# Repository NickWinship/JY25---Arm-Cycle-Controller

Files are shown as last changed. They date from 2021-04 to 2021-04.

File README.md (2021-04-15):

# Xbox One Arm-Cycle-Controller

The Xbox One Arm-Cycle-Controller is an exercise device that interfaces with the Xbox Adaptive Controller to produce an interactive fitness experience targeted towards users with spinal cord injuries. 

The device functions as an electromechanical adapter that adds controller functionality to a commercial mini-exercise bicycle through the use of control signals derived from encoder and inertial measurements. The control signals are interpreted by the Xbox Adaptive Controller as joystick and trigger inputs, allowing the device to play racing games on Xbox One Series consoles or Windows 10 PCs.

## Project Background
Individuals with physical disabilities often have limited options to be physically active. A popular form of cardiovascular exercise for people with Spinal Cord Injuries (SCIs) is ‘hand cycling’. At the Physical Activity Research Centre (PARC), users with SCIs can engage in many physical exercise activities while building social connections within their community. 

With the ongoing COVID-19 situation and the initial closure of PARC, it was clear that there was a need for a new home-based exercise device for individuals with SCIs. The goal of this Capstone project, was to develop an Arm Cycle Controller, compatible with the Xbox adaptive controller for Xbox One Series consoles and Windows 10 PCs. The final product is aimed at bringing an inexpensive and engaging exercise experience into the end user’s home, one that can foster community through online engagement. 

## Compatibility
| Device | Version | Additional Information|
|--------|---------|-----------------------|
|Xbox Console| One Series | |
| PC | Windows 10.0 | |

## Download
| Resrouce | Version | Format | Link |
|----------|---------|--------|------|
| PCB Files |
| Firmware |
| PCB Housing |
| MPU6050 Housing |
| Encoder Mount |

## Resources
| Resrouce | Link |
|----------|------|
| Project Instrucable| https://www.instructables.com/How-to-Build-Your-Xbox-One-Arm-Cycle-Adaptive-Cont/ |
|Project Video | https://www.youtube.com/watch?v=MWBfiwAXUjg |

## Contributers
***Clients/Sponsers:***
<ul>
  <li>PARC (Physical Activity Research Centre) [https://icord.org/parc/]</li>
  <li>Makers Making Change [https://www.makersmakingchange.com/]</li>
  <li>Microsoft [https://www.microsoft.com/en-us/accessibility]</li>
</ul>

***Capstone Students:***
<ul>
  <li>Scott Beaulieu [nicholassjbeaulieu@protonmail.com]</li>
  <li>Edward Luo [luohaoubc@gmail.com]</li>
  <li>Keith Consolacion [keithcon@student.ubc.ca]</li>
  <li>Fabian Lozano [fabian.lozano@protonmail.com]</li>
  <li>Nicholas Winship [nick.winship@outlook.com]</li>
</ul>

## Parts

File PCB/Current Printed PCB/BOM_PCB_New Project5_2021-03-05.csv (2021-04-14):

ID | Name | Designator | Footprint | Quantity | Manufacturer Part | Manufacturer | Supplier | Supplier Part | JLCPCB SMD | LCSC Assembly | Assembly Type | Paste Type
1 | WJ128V-5.0-3P | E1 | CONN-TH_3P-P5.00_WJ128V-5.0-3P | 1 | WJ128V-5.0-3P | ReliaPro | LCSC | C8270 |  | Yes | manualWeld | expand
2 | WJ128V-5.0-2P | E2 | CONN-TH_2P-P5.00_WJ128V-5.0-2P | 1 | WJ128V-5.0-2P | ReliaPro | LCSC | C8269 |  | Yes | manualWeld | expand
3 | DB125-3.81-4P | IMU,JJ1 | CONN-TH_DB125-3.81-4P | 2 | DB125-3.81-4P | DIBO | LCSC | C395880 |  | Yes | manualWeld | expand
4 | PJ313D | JL1,JR1 | AUDIO-TH_PJ313D | 2 | PJ313D | BOOMELE | LCSC | C18167 |  | Yes | manualWeld | expand
5 | 1K | J1,J2,L1,L3,R1,R3 | R0603 | 6 | 0603WAF1001T5E | UniOhm | LCSC | C21190 | Yes | Yes | smtWeld | base
6 | 10K | J3,J4,L2,R2 | R0603 | 4 | 0603WAF1002T5E | UniOhm | LCSC | C25804 | Yes | Yes | smtWeld | base
7 | TEENSY 4.0 W/O int Pins | T1 | TEENSY 4.0 W/O INT PINS | 1 | Teensy 4.0 | PJRC

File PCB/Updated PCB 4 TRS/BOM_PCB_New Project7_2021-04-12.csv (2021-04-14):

ID | Name | Designator | Footprint | Quantity | Manufacturer Part | Manufacturer | Supplier | Supplier Part | Price | LCSC Assembly | Assembly Type | Paste Type | JLCPCB SMD
1 | WJ128V-5.0-3P | E1 | CONN-TH_3P-P5.00_WJ128V-5.0-3P | 1 | WJ128V-5.0-3P | ReliaPro | LCSC | C8270 | 0.1393 | Yes | manualWeld | expand
2 | WJ128V-5.0-2P | E2 | CONN-TH_2P-P5.00_WJ128V-5.0-2P | 1 | WJ128V-5.0-2P | ReliaPro | LCSC | C8269 | 0.091 | Yes | manualWeld | expand
3 | DB125-3.81-4P | IMU | CONN-TH_DB125-3.81-4P | 1 | DB125-3.81-4P | DIBO | LCSC | C395880 | 0.1909 | Yes | manualWeld | expand
4 | 10K | J2,J5,L2,R2 | R0603 | 4 | 0603WAF1002T5E | UniOhm | LCSC | C25804 | 0.001 | Yes | smtWeld | base | Yes
5 | 1K | J1,J3,J4,J6,L1,L3,R1,R3 | R0603 | 8 | 0603WAF1001T5E | UniOhm | LCSC | C21190 | 0.001 | Yes | smtWeld | base | Yes
6 | PJ313D | JL,JR,JR1,JR2 | AUDIO-TH_PJ313D | 4 | PJ313D | BOOMELE | LCSC | C18167 | 0.057 | Yes | manualWeld | expand
7 | TEENSY 4.0 W/O int Pins | T | TEENSY 4.0 W/O INT PINS | 1 | Teensy 4.0 | PJRC

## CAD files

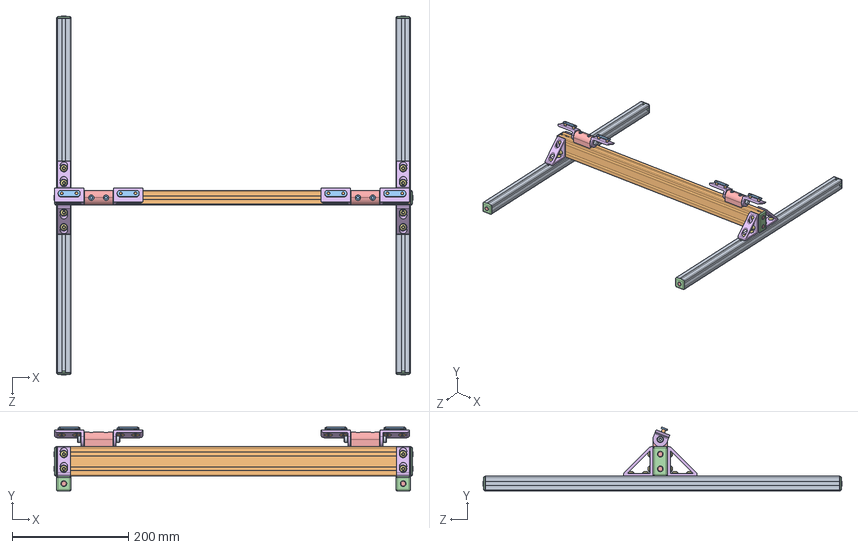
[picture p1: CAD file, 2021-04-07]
3D Prints/Arm Cycle Mount Models/Arm Cycle Controller.sldasm
618.1 x 110.1 x 618.1 mm
SHCS x 4
Dynamic L Pivot Arms x 4
10S Large Washer x 4
10S Small Washer x 4
Socket Head Shoulder Screw_AI x 4
Socket Countersunk Head Cap Screw_AI x 8
TSLOT ENDCAPS x 6
Inside Corner Gussets x 4
Socket Button Head Cap Screw_AI x 16

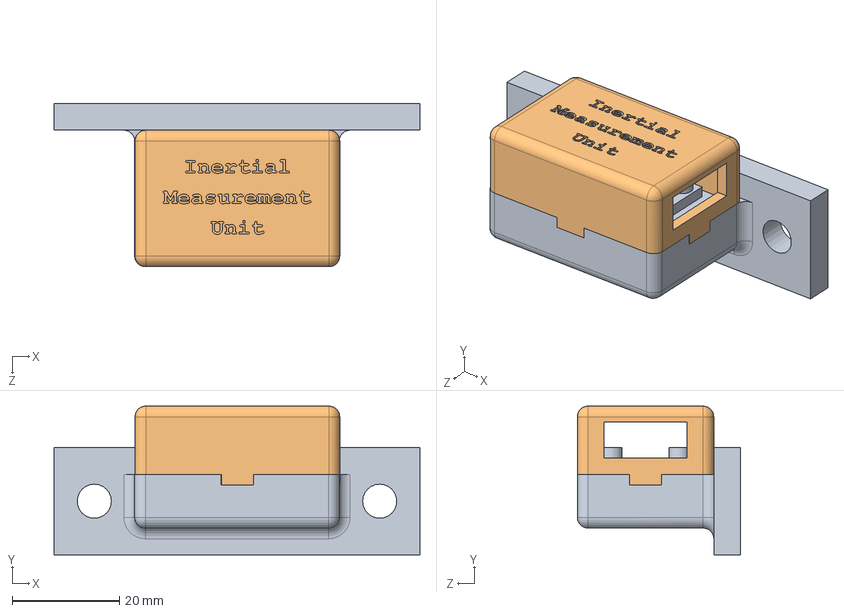
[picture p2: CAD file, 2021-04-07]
3D Prints/MPU6050 Mount Models/MPU6050 Mount Assembly.SLDASM
68.1 x 27.7 x 30.4 mm
MPU6050 Mount
Cover

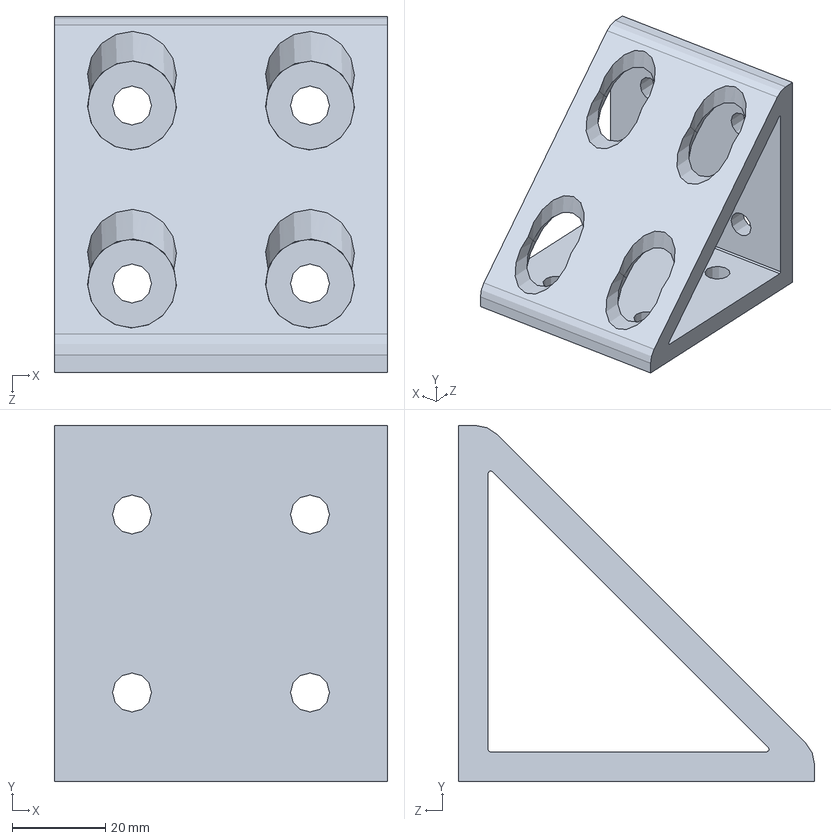
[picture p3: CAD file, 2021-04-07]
3D Prints/Arm Cycle Mount Models/Inside Corner Gussets.SLDASM
71.4 x 76.2 x 76.2 mm

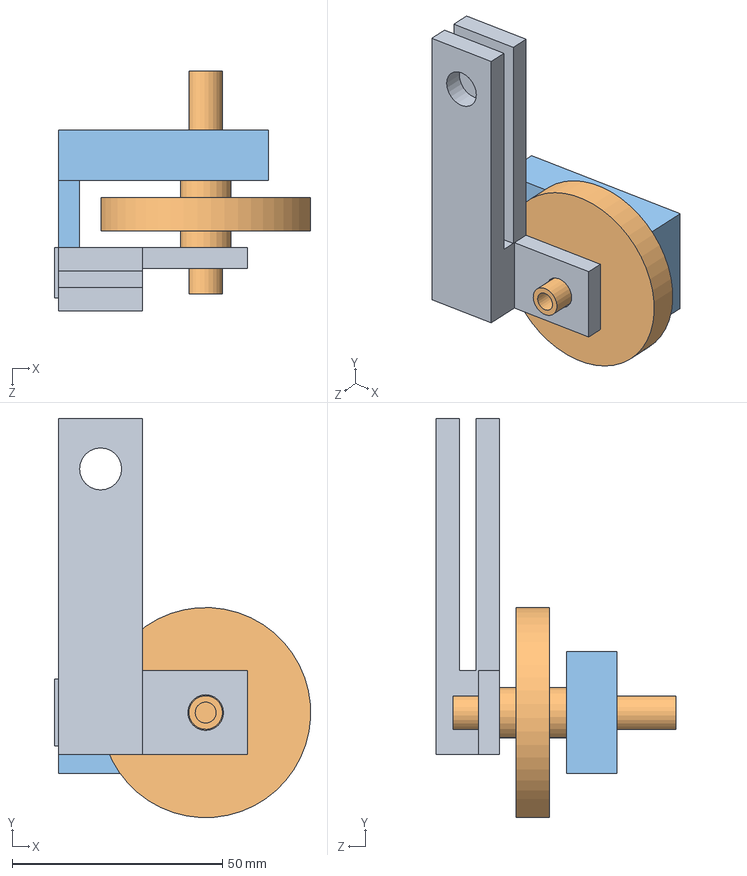
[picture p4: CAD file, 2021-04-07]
3D Prints/Encoder Mount Models/Encoder Attatchment Assembly.SLDASM
61.0 x 94.9 x 57.0 mm
Mounting
Gear
Wheel support

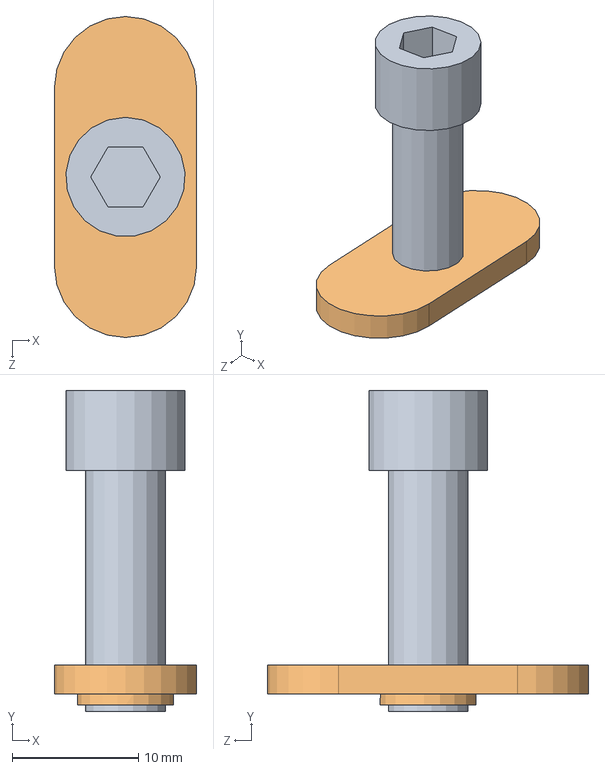
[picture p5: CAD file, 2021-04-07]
3D Prints/Arm Cycle Mount Models/SHCS Assembly.SLDASM
11.3 x 25.4 x 25.4 mm
SHCS
Economy T-nuts

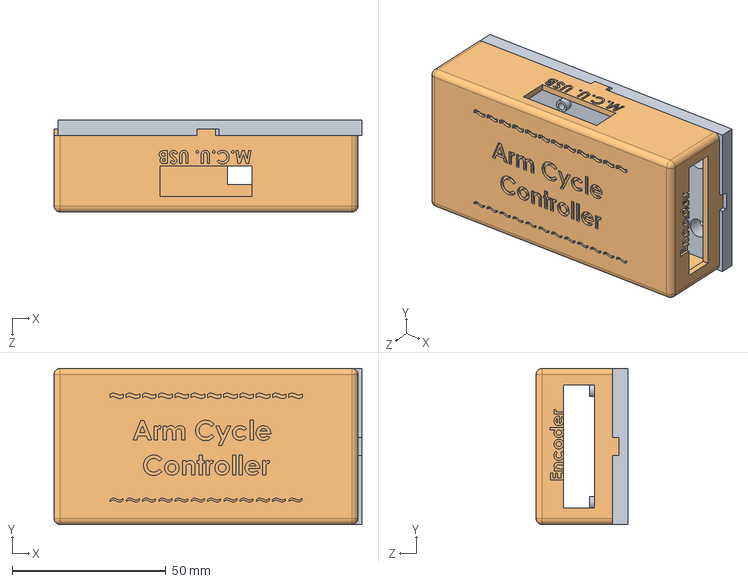
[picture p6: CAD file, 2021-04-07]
3D Prints/PCB Mount Models/PCB Mount Assembly.SLDASM
100.3 x 50.8 x 30.0 mm
PCB Mount
PCB Cover

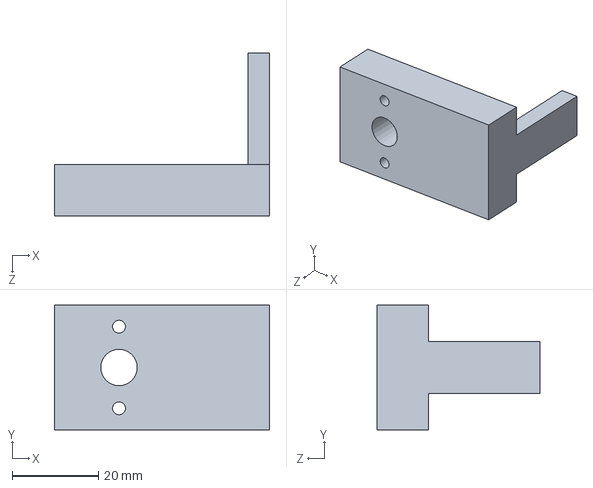
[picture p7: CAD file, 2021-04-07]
3D Prints/Encoder Mount Models/Wheel support.SLDPRT
50.0 x 29.0 x 38.0 mm

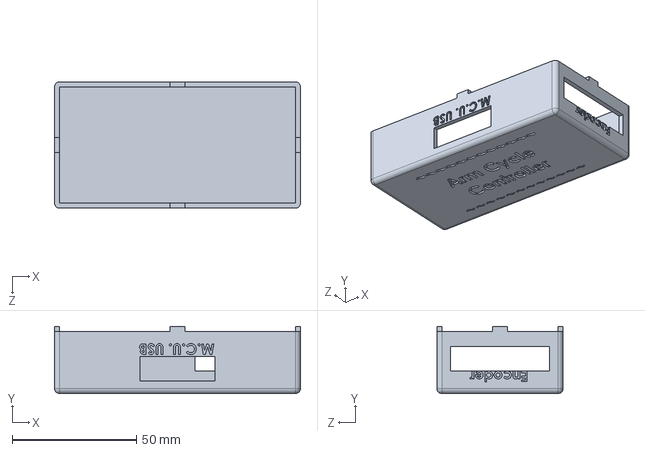
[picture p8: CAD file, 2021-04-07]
3D Prints/PCB Mount Models/PCB Cover.SLDPRT
99.0 x 27.0 x 50.8 mm

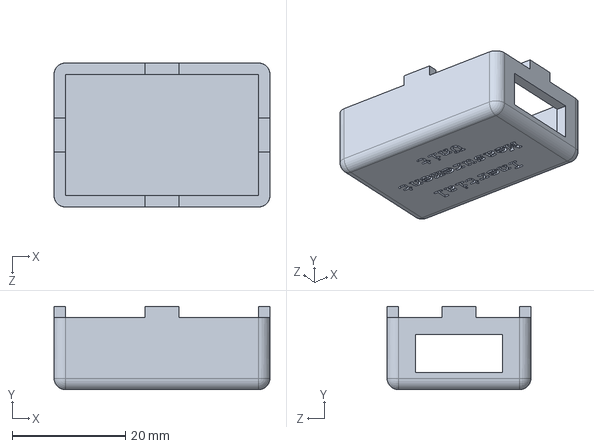
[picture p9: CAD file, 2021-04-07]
3D Prints/MPU6050 Mount Models/Cover.SLDPRT
38.1 x 14.7 x 25.4 mm

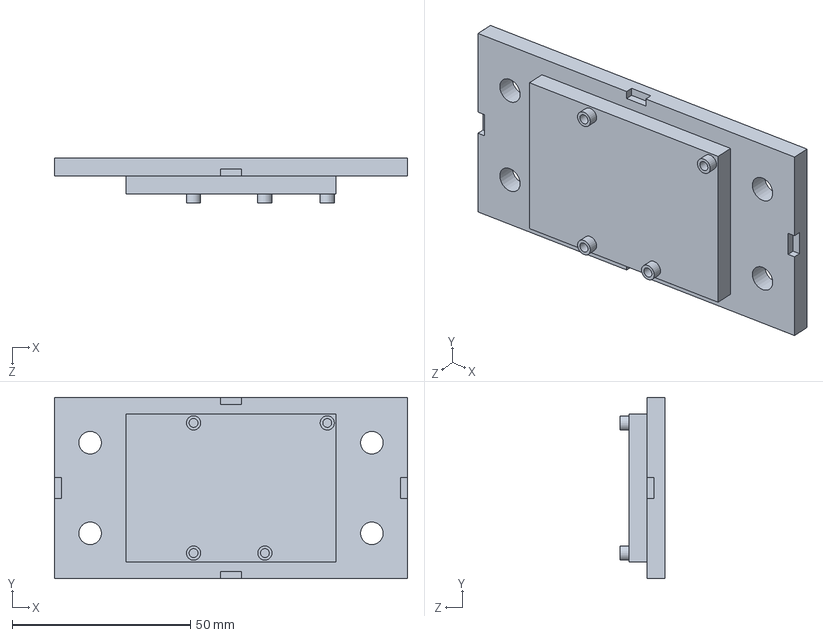
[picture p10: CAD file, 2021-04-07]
3D Prints/PCB Mount Models/PCB Mount.SLDPRT
99.0 x 50.8 x 12.5 mm

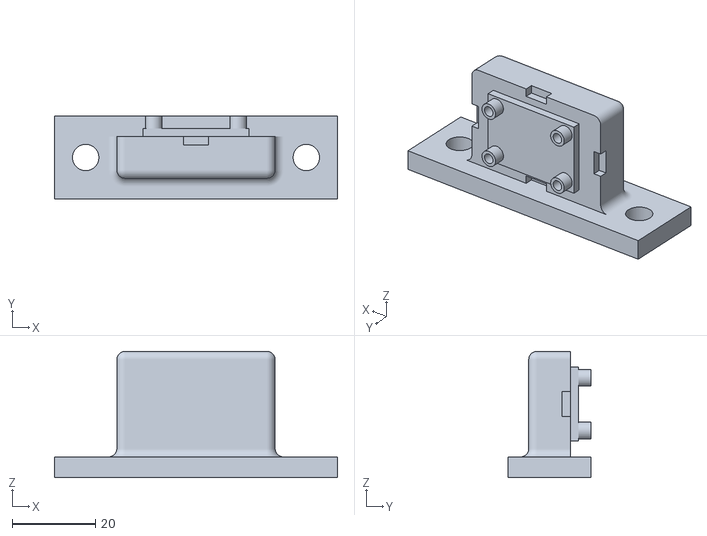
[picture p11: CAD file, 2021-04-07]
3D Prints/Project STL Files/IMU_Mount_1.STL
68.1 x 20.0 x 30.4

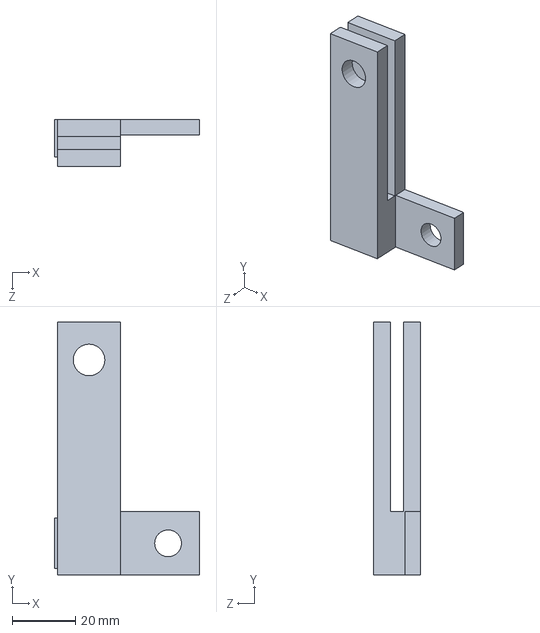
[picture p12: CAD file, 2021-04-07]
3D Prints/Encoder Mount Models/Mounting.SLDPRT
46.0 x 80.0 x 15.0 mm

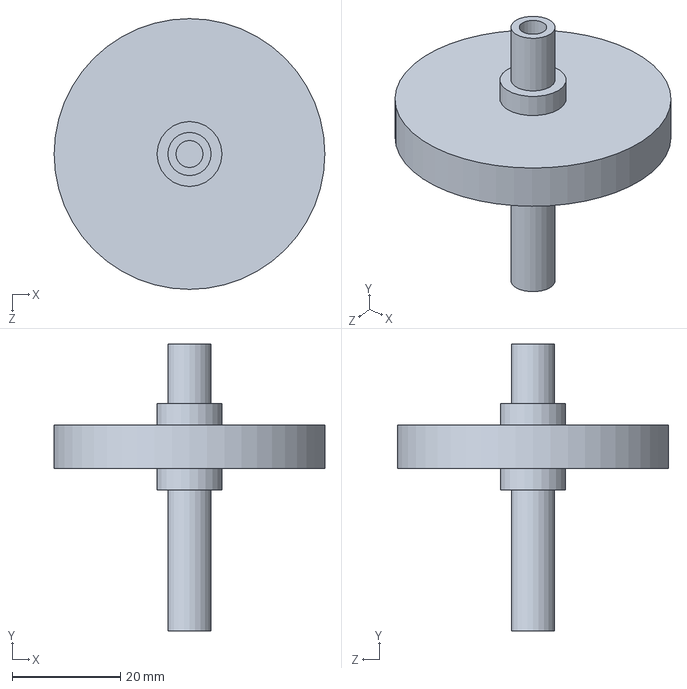
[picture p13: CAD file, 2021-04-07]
3D Prints/Encoder Mount Models/Gear.SLDPRT
50.0 x 53.0 x 50.0 mm

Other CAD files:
3D Prints/Project STL Files/PCB_Mount_2.STL
3D Prints/MPU6050 Mount Models/MPU6050 Mount.SLDPRT
3D Prints/Project STL Files/Encoder_Mount_2.STL
3D Prints/Project STL Files/Encoder_Mount_3.STL
3D Prints/Project STL Files/PCB_Mount_1.STL
3D Prints/Arm Cycle Mount Models/10S Large Washer.SLDPRT
3D Prints/Arm Cycle Mount Models/10S Small Washer.SLDPRT
3D Prints/Arm Cycle Mount Models/650000.SLDPRT
3D Prints/Arm Cycle Mount Models/650002.SLDPRT
3D Prints/Arm Cycle Mount Models/651021.SLDASM
3D Prints/Arm Cycle Mount Models/651029.SLDASM
3D Prints/Arm Cycle Mount Models/651084 Push In Fastener.SLDPRT
3D Prints/Arm Cycle Mount Models/651084.SLDPRT
3D Prints/Arm Cycle Mount Models/651099.SLDPRT
3D Prints/Arm Cycle Mount Models/651119.SLDASM
3D Prints/Arm Cycle Mount Models/651130 FBHSCS & Economy T-Nut.SLDASM
3D Prints/Arm Cycle Mount Models/651130.SLDASM
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

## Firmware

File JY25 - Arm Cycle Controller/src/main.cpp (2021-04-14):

// INCLUDE LIBRARIES
#include <Arduino.h>
#include <Adafruit_MPU6050.h>
#include <Adafruit_Sensor.h>
#include <Encoder.h>
#include <Wire.h>

// DEFINITIIONS ---------------------------------------------------------
#define INDEX_PULSE 21
#define ENCODER_PIN_A 23
#define ENCODER_PIN_B 22
#define LED_PIN 13

/* PIN DEFINITIONS */
#define RT_REF_PIN PIND3
#define LT_REF_PIN PIND4
#define JOYSTICK_REF_PIN PIND5

#define LB_PIN PIND7
#define RB_PIN PIND6
#define JOYSTICK_RIGHT 9
#define JOYSTICK_LEFT 8

#define MAX_DUTY_CYCLE 65

#define PPR 192.0              // (48ppr x 4 = 192)(quadrature)
#define PPR_ARM_CYCLE PPR*3
#define ONE_SECOND_MICRO  1000000.00    // (1sec in microseconds)
#define MAX_CPS 3.0 
#define MAX_TILT 5.0

// ENCODER OBJECTS ------------------------------------------------------
Encoder ArmCycle(ENCODER_PIN_A, ENCODER_PIN_B);
elapsedMicros sinceEncoderUpdate;

// IMU OBJECTS ----------------------------------------------------------
Adafruit_MPU6050 mpu;

// GLOBAL VARIABLES -----------------------------------------------------
volatile long encoderPosition  = -999;

/**
 * @brief Sets the duty cycle of the forward or backwards movement pins.
 * 
 * @param dutyCycle The target duty cycle
 * @param isForward Flag indicating whether the target cranking direction is forward
 */
void SetCrankingSpeedDirection(unsigned char dutyCycle, bool isForward = true) {
    // cap the duty cycle at the maximum value
    if(dutyCycle > MAX_DUTY_CYCLE) 
        dutyCycle = MAX_DUTY_CYCLE;

    if(isForward) {
        // output voltage to pin connected to RB trigger 
        analogWrite(LB_PIN, 0); 
        analogWrite(RB_PIN, (int)dutyCycle);
    }
    else {
        // output voltage to pin connected to LB trigger
        analogWrite(RB_PIN, 0);
        analogWrite(LB_PIN, (int)dutyCycle);
    }
}

/**
 * @brief Set the direction and magnitude of the simulated joystick's movement.
 * 
 * @param dutyCycle The target duty cycle
 * @param direction The joystick direction. Center is 0, right is 1 and left is 2.
 */
void SetJoystickVector(unsigned char dutyCycle, unsigned char direction = 0) {
    // check whether a valid direction was specified
    if(direction < 0 || direction > 2) return;

    // cap the duty cycle at the maximum value
    if(dutyCycle > MAX_DUTY_CYCLE) 
        dutyCycle = MAX_DUTY_CYCLE;

    // set the duty cycle according to the direction specified:

    // CENTERED
    if(direction == 0) {
        analogWrite(JOYSTICK_RIGHT, 0);
        analogWrite(JOYSTICK_LEFT, 0);
    }

    // RIGHT
    else if(direction == 1) {
        analogWrite(JOYSTICK_RIGHT, (int)dutyCycle);
        analogWrite(JOYSTICK_LEFT, 0);
    }

    // LEFT
    else {
        analogWrite(JOYSTICK_RIGHT, 0);
        analogWrite(JOYSTICK_LEFT, (int)dutyCycle);
    }
}

/**
 * @brief Setup function that runs once upon startup
 * 
 */
void setup() {

    // configure output pins
    pinMode(RT_REF_PIN, OUTPUT);
    pinMode(LT_REF_PIN, OUTPUT);
    pinMode(JOYSTICK_REF_PIN, OUTPUT);

    pinMode(RB_PIN, OUTPUT);
    pinMode(LB_PIN, OUTPUT);
    pinMode(JOYSTICK_RIGHT, OUTPUT);
    pinMode(JOYSTICK_LEFT, OUTPUT);
    
    // set the initial cranking speed to 0
    SetCrankingSpeedDirection(0, true);

    // place the joystick in the centre position
    SetJoystickVector(0, 0);

    // output 1.8V out of the analog reference voltage pins
    analogWrite(RT_REF_PIN, MAX_DUTY_CYCLE);
    analogWrite(LT_REF_PIN, MAX_DUTY_CYCLE);
    analogWrite(JOYSTICK_REF_PIN, MAX_DUTY_CYCLE);

    // put the the joystick in the center position
    analogWrite(JOYSTICK_RIGHT, 0);
    analogWrite(JOYSTICK_LEFT, 0);

    // set Teensy 4.0 pins
    pinMode(ENCODER_PIN_A, INPUT);  // encoder channel A
    pinMode(ENCODER_PIN_B, INPUT);  // encoder channel B
    pinMode(LED_PIN, OUTPUT);           // on board LED

    // initialize serial communication at 115200 bits per second
    Serial.begin(115200);

    // attempt to initialize the MPU
    if (!mpu.begin()) {
        Serial.println("Failed to find MPU6050 chip");

    }
    else {
        Serial.println("MPU6050 Found!");

        mpu.setAccelerometerRange(MPU6050_RANGE_8_G);
        Serial.print("Accelerometer range set to: ");
        switch (mpu.getAccelerometerRange()) {
        case MPU6050_RANGE_2_G:
            Serial.println("+-2G");
            break;
        case MPU6050_RANGE_4_G:
            Serial.println("+-4G");
            break;
        case MPU6050_RANGE_8_G:
            Serial.println("+-8G");
            break;
        case MPU6050_RANGE_16_G:
            Serial.println("+-16G");
            break;
        }

        mpu.setGyroRange(MPU6050_RANGE_500_DEG);
        Serial.print("Gyro range set to: ");
        switch (mpu.getGyroRange()) {
        case MPU6050_RANGE_250_DEG:
            Serial.println("+- 250 deg/s");
            break;
        case MPU6050_RANGE_500_DEG:
            Serial.println("+- 500 deg/s");
            break;
        case MPU6050_RANGE_1000_DEG:
            Serial.println("+- 1000 deg/s");
            break;
        case MPU6050_RANGE_2000_DEG:
            Serial.println("+- 2000 deg/s");
            break;
        }

        mpu.setFilterBandwidth(MPU6050_BAND_21_HZ);
        Serial.print("Filter bandwidth set to: ");
        switch (mpu.getFilterBandwidth()) {
        case MPU6050_BAND_260_HZ:
            Serial.println("260 Hz");
            break;
        case MPU6050_BAND_184_HZ:
            Serial.println("184 Hz");
            break;
        case MPU6050_BAND_94_HZ:
            Serial.println("94 Hz");
            break;
        case MPU6050_BAND_44_HZ:
            Serial.println("44 Hz");
            break;
        case MPU6050_BAND_21_HZ:
            Serial.println("21 Hz");
            break;
        case MPU6050_BAND_10_HZ:
            Serial.println("10 Hz");
            break;
        case MPU6050_BAND_5_HZ:
            Serial.println("5 Hz");
            break;
        }

        Serial.println("");
        delay(100);
    }

}

/**
 * @brief Main execution loop.
 * 
 */
void loop() {
    
    long newEncoderPosition;
    double PPS, armCycleCPS;
    unsigned char cyclingDutyCycle;
    bool isCycleDirectionForward;
    unsigned char steeringDutyCycle;
    unsigned char SteeringDirection;

    sensors_event_t a, g, temp;

    mpu.getEvent(&a, &g, &temp);

    // calculate the duty cycle and direction of the joystick based on steering position
    // RIGHT
    if(a.acceleration.y < -1){
        SteeringDirection = 1;
        steeringDutyCycle = (abs(a.acceleration.y) / MAX_TILT) * MAX_DUTY_CYCLE;
    }

    // LEFT
    else if(a.acceleration.y > 1){
        SteeringDirection = 2;
        steeringDutyCycle = (abs(a.acceleration.y) / MAX_TILT) * MAX_DUTY_CYCLE;
    }

    // CENTER
    else{
        SteeringDirection = 0;
        steeringDutyCycle = 0;
    }

    // output voltage and direction representing joystick position to controller
    SetJoystickVector(steeringDutyCycle, SteeringDirection);

    // read the encoder position
    newEncoderPosition = ArmCycle.read();

    if (newEncoderPosition != encoderPosition) {

        // Pulses per second
        PPS = ((double)newEncoderPosition - (double)encoderPosition)*ONE_SECOND_MICRO / (double)sinceEncoderUpdate;
        
        // calculate the speed in cycles per second
        armCycleCPS = PPS / (PPR*3); // It's roughly 3x encoder per arm cycle revolution

        // determine the cycling direction
        isCycleDirectionForward = armCycleCPS < 0 ? false : true;

        // calculate the level of trigger depression using the current CPS
        cyclingDutyCycle = (abs(armCycleCPS) / MAX_CPS) * MAX_DUTY_CYCLE;

        // update new position
        encoderPosition = newEncoderPosition;

        // set the duty cycle of the respective pin
        SetCrankingSpeedDirection(cyclingDutyCycle, isCycleDirectionForward);

        // Reset time between encoder increments
        sinceEncoderUpdate = 0;
    }

}

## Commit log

2021-01-14 Added initial encoder sensor code
2021-01-15 Initial Power PCB
    [PCB1.PcbDoc, PCB_Project1.PrjPCB, Sheet1.SchDoc]
2021-02-05 Second PCB
    [PCB12.PcbDoc, PCB_Project12.PrjPCB, Sheet12.SchDoc]
2021-03-03 Milestone 3
    [PCB13.PcbDoc, PCB_Project13.PrjPCB, Sheet13.SchDoc]
2021-03-19 Fix swapped pin connections
2021-04-07 Added 3D Printed Model Files
    Added STL Files and Solidworks Models of the 3D printed parts
    [Cover.SLDPRT, Encoder Attatchment Assembly.SLDASM, Encoder_Mount_1.STL, Encoder_Mount_2.STL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]
2021-04-07 Added the Arm Cycle Mount T-slot Model
    Added the Arm Cycle Mount T-slot Solidworks model. This model was made using the T-slots DesignPro plugin for solidworks. The plugin is available here: https://www.tslots.com/designpro/
    [10S Large Washer.SLDPRT, 10S Small Washer.SLDPRT, 650000.SLDPRT, 650002.SLDPRT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]
2021-04-08 Exported from EasyEDA
    [Current Printed PCB, Altium.pcbdoc, Update PCB (4 TRS), Altium.pcbdoc]
2021-04-12 Current printed PCB related files mainly EasyEDA
    [BOM_PCB_New Project5_2021-03-05.csv, Current Printed PCB, Altium.pcbdoc, PickAndPlace_PCB_New Project5_2021-03-05.csv]
2021-04-12 Updated PCB, 4 TRS, mainly EasyEDA
    [BOM_PCB_New Project7_2021-04-12.csv, PickAndPlace_PCB_New Project7_2021-04-12.csv, Update PCB (4 TRS), Altium.pcbdoc]
2021-04-14 Updated PCB, 4 TRS mainly EasyEDA
    [BOM_PCB_New Project7_2021-04-12.csv, PickAndPlace_PCB_New Project7_2021-04-12.csv, Update PCB (4 TRS), Altium.pcbdoc]
2021-04-14 Move PCB files and folders to single main folder
    [BOM_PCB_New Project5_2021-03-05.csv, BOM_PCB_New Project7_2021-04-12.csv, Current Printed PCB, Altium.pcbdoc, PCB1.PcbDoc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]
